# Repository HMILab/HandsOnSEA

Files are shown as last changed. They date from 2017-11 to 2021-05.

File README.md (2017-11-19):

# HandsOn-SEA

HandsOn-SEA is a single degree of freedom educational robot that features series elastic actuation and relies on closed loop force control to achieve the desired level of safety and transparency during physical interactions. HandsOn-SEA complements the existing impedance-type Haptic Paddle designs by demonstrating the challenges involved in the synergistic design and control of admittance-type devices. HandsOn-SEA can be used to allow students to experience the performance trade-offs inherent in force control systems, due to the non-collocation between the force sensor and the actuator.

For more information and videos please follow the [link](http://hmi.sabanciuniv.edu/?page_id=992).

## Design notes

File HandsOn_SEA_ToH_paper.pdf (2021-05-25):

IEEE TRANSACTIONS ON HAPTICS, VOL. X, NO. X, MAY 2021 | 1

# Physical Human-Robot Interaction Using HANDSON-SEA: An Educational Robotic Platform with Series Elastic Actuation

Ata Otaran | Ozan Tokatli | Volkan Patoglu

Abstract—For gaining proficiency in physical human-robot interactions, it is crucial for engineering students to be provided with the opportunity to gain hands-on experience with robotic devices that feature kinesthetic feedback. We propose HandsOn-SEA, a low-cost, single degree-of-freedom, force-controlled educational robot with series elastic actuation and introduce educational modules for the use of the device to allow students to experience the fundamental performance trade-offs inherent in robotic systems. The novelty of the proposed robot is due to the deliberate introduction of a compliant element between the actuator and the handle, whose deflections are measured to perform closed-loop force control. As an admittance-type robot, HandsOn-SEA relies on force feedback to achieve the desired level of safety and transparency and complements the existing impedance-type educational robots. We present the integration of HandsOn-SEA into the robotics curriculum, by providing guidelines for its use in a senior level robotics course, to help students experience the challenges involved in the synergistic design and control of robotic devices. We systematically evaluate the efficacy of the device in a robotics course delivered for five semesters and provide evidence that HandsOn-SEA is effective in instilling fundamental concepts and trade-offs in the design and control of robotic devices.

Index Terms—Physical Human-Robot Interaction (pHRI), Series Elastic Actuation (SEA), Educational Robotics, Interaction Control

I. INTRODUCTION
Establishing natural and safe physical human-robot interactions (pHRI) is an active research area. A thorough understanding of such interactions can be the basis of successful applications in many areas, including service robotics, surgical, assistive and rehabilitative robotics, haptics and teleoperation. Therefore, it is important for engineering students to have the opportunity to physically interact with robots to gain hands-on experience in their design and control. Hands-on experience is known to be crucial in strengthening the understanding of basic engineering concepts [1]. Haptic paddles [2]—single degree-of-freedom (DoF) devices with kinesthetic feedback—have been successfully utilized as effective teaching platforms for several system dynamics and controls classes in many universities around the world [3]. As educational tools, all haptic paddles share the common design features of simplicity, robustness and low cost. Design simplicity allows students to easily understand the working principles, while robustness and low cost enable their accessibility and availability for large groups of students.
In this paper, we introduce an educational force-feedback robot and provide guidelines for the educational use of the device to demonstrate the synergistic nature of mechanical design and control in robotic devices. We also present a set of laboratory assignments that allow students to experience the interdependency of design choices in the mechatronic design of robotic systems. These laboratory assignments require students to modify the mechanical system, in addition to its controller and characterize the effects of these design decisions on the closed-loop control performance of the educational device. We evaluate the efficacy of introducing HANDSON-SEA into robotics education by testing the device in a senior level robotics course delivered over five semesters and provide evidence that the
A. Otaran, O. Tokatli and V. Patoglu are with the Faculty of Engineering and Natural Sciences of Sabancı University, ˙Istanbul, Turkey.
E-mail: {ataotaran,otokatli,volkan.patoglu}@sabanciuniv.edu
Manuscript received May 30, 2020 and revised March 25, 2021.

device is effective in providing experience on fundamental concepts in robot control and instilling in a strong understanding of fundamental trade-offs in the design and control of force-feedback robotic devices. In comparison to its preliminary conference version [4], this paper details the mechatronics design, control, and performance of the device; significantly extends the guidelines for its educational use; evaluates the instructional design of the laboratory sessions through the achievement of course learning outcomes; and provides a systematic long-term evaluation of student performance and a comparison of this performance to a control group.

II. RELATED WORK

A. Design of Educational Devices with Haptic Feedback

Several open-hardware designs concerning force controlled robots exist in the literature. A pioneering educational force controlled robot designed for kinesthetic feedback is the haptic paddle [2]. The haptic paddle is a single DoF impedance-type device that features passive backdrivability and excellent transparency, thanks to its low apparent inertia and negligible power transmission losses. In the original design, a Hall effect sensor is used to sense rotations, while a custom built (analog) linear current amplifier is utilized to avoid torque ripple associated with PWM type motor drives. Other important design features of the haptic paddle are its robust design and low cost, thanks to utilization of common off-the shelf parts and simple rapid prototyping methods for its construction.
The success of this design has led to several different versions of the haptic paddle [5]–[10]. The original haptic paddle design relies on a capstan drive. However, the maintenance of the capstan transmission after cable stretch, fall-off or break is a tedious task, especially for an educational setup. To address these problems, the capstan transmission of the original design has been replaced by a custom built direct drive voice coil actuation in iTouch [5], [11], while a friction drive transmission has been adapted in [8].
In [6], improvements have been implemented to increase the design robustness and to decrease the manufacturing cost of haptic paddle. Further design iterations have been undertaken in [7], [9], [10], where especially the underlying electronics and control interface have been modified and updated. In particular, most of the earlier designs rely on PC based I/O cards and linear current amplifiers, while analog controller circuits are utilized in [5]. A PWM voltage amplifier and an Atmel processor (Arduino) based micro-controller are adapted in [8], trading-off the fast control rates of PC based controllers and torque control performance of linear current amplifiers with a more compact and low cost control/power electronics infrastructure. A recent iteration of these designs, the Hapkit [10], further customizes the control/power electronics infrastructure proposed in [8] and adds a force sensitive resistor to the device handle.
Haptic paddles aim at establishing safe and transparent pHRI. To achieve these goals, all of the designs reported in the literature rely on low inherent output impedance of the mechanical device. In particular, all of the existing haptic paddle designs are of impedance-type, possessing passive backdrivability thanks to their low friction power transmissions and low apparent inertia. Such impedance-type devices are commonly preferred for haptic interactions, since these devices can achieve high force control fidelity even with open-loop force control, that is, without the need for force feedback.
While HANDSON-SEA preserves the simplicity, robustness and low cost of other designs, as an admittance-type robotic device, it is fundamentally different from and complementary to all of the existing haptic paddles, as force feedback is an inherent design feature of HANDSON-SEA. Thanks to its integrated force estimation mechanism, HANDSON-SEA can utilize force feedback to modulate its output impedance for high fidelity haptic rendering. Due to its high transmission ratio, HANDSON-SEA is capable of rendering large forces at its handle, producing strong kinesthetic feedback that is easily differentiable by its users. As a result of its integrated force sensing element, HANDSON-SEA is inherently compliant, resulting in safe interactions even under impacts. The stiffness of the compliant element has a direct and observable effect on the performance of HANDSON-SEA and this compliance needs to be considered as part of its dynamic model and model based controllers.
B. Evaluation of Educational Devices with Haptic Feedback

Haptic paddles have been adopted to engineering curriculum by several universities [3]. The first investigation of a haptic paddle type device in a classroom/laboratory environment was conducted in [2]. In this work, haptic paddle has been proposed to support the learning process of students who have dominant haptic cognitive learning styles. The device was used for an undergraduate course on dynamic systems for a semester at Stanford University. The laboratory exercises included motor spin down test for observing the damping effect, bifilar pendulum test for understanding the components of the dynamic system, sensor calibration and motor constant determination, impedance control and virtual environment implementations. The laboratory modules of this work have formed a basis for other courses taught in different universities. The effectiveness of the haptic paddle was measured by a student survey and it has been observed that the device helped students to better grasp engineering concepts.
At the University of Michigan, force controlled devices iTouch and Box were used in engineering undergraduate courses [5]. In a mechanical engineering course, the device was used to support the learning of students about concepts such as frequency domain representations, dynamical system modeling and haptic interactions. In an electrical engineering course, students were introduced to integrating sensors and actuators to micro-controllers, learned about hybrid dynamical systems and improved their programming skills. Haptic paddle was also used in an undergraduate system dynamics course at Rice University [6], [12]. The use of the device aimed to improve the effectiveness of the laboratory sessions and to introduce students to haptic systems, where virtual environments can be used to assist the teaching of complex dynamics phenomena. In [6], student understanding of engineering concepts and fundamentals was quantified through a 16-item grading rubric during two semesters: a semester with traditional laboratory sessions disjointed from the course material and another semester during which haptic paddle was introduced to conduct a cohesive set of laboratory exercises. Results indicated important gains in student understanding with the integration of cohesive set of laboratory exercises with haptic paddles. In [12], a formal analysis was conducted over two semesters to investigate the effect of inclusion of reflective learning activities implemented through pre- and post-lab discussions. Performance was quantified through rubics, homework, laboratory, and final exam grades. Statistical analysis revealed that laboratory exercises with reflective learning activities resulted in statistically significant performance increase on the overall laboratory grades. While a significant effect was not shown for the final grades, reflective learning activities improved standard deviations and resulted in higher lowest grades. Another systematic evaluation of integrating haptic paddle in an undergraduate level pHRI course has been conducted in [7]. The pHRI course covered the effect of having a human in the loop, the design methodology for pHRI systems, system identification for the robotic devices, force controller design and assessment of the robot performance in terms of psychophysical metrics. Laboratory sessions included the implementation of open-loop and close-loop impedance controllers, gravity and friction compensation methods, and interaction controllers. Moreover, students were asked to complete course projects that combined the concepts they learned throughout the lectures. The effectiveness of the haptic paddle based instruction was measured by student evaluation surveys, oral exams and student presentations. It has been observed that hands-on learning was beneficial for pHRI and laboratory sessions can help students achieve higher degree of knowledge synthesis according to the Structure of Observed Learning Outcomes (SOLO) taxonomy. Furthermore, students’ evaluations of the device were positive, while the instructors observed an improved success rate in their exams.
Haptic paddle has also been used in an undergraduate system dynamics course at Vanderbilt University [8]. The laboratory sessions included analyzing first and second order system models, determining equivalent mass, damping and stiffness of these systems, exploring friction/damping and other external disturbances and observing their effects on the output of the system, experiencing the forced responses of vibratory systems, and implementing several closed-loop controllers. A formal assessment of student learning due to haptic paddle integration to the course was conducted over three semesters. To quantify student learning, assessments were administered before and after each semester. Furthermore, to determine the timing of learning, five multiple choice quizzes were administered in a randomized manner, before the lab, after the pre-lab, after the lab and after completing the lab report. Results showed a statistically significant difference with a large effect size between the cumulative scores at the beginning and at the end of the semester evaluations, indicating that students have gained a better understanding of and displayed better retention rates for the majority of the core concepts they learned throughout the course via all learning opportunities. The statistical analysis also revealed that supplementing the in-class lectures with laboratory sessions as a whole (including pre-lab, during lab, and lab report activities) enhanced student understanding of the material. The Stanford haptic paddle, called Hapkit, has been integrated as the main experimental setup in a massive open online course made accessible all around the world [10]. A newer version of Hapkit has also been used to teach physics in secondary education [13]. HANDSON-SEA complements all of these existing haptic paddles, not only in terms of its mechatronic design, but also as an educational tool, by enabling students to experience force-feedback control architectures for pHRI, and by demonstrating the synergistic design challenges involved in the mechatronic design of robotic devices. While HANDSON-SEA can be used to administer the laboratory exercises during a systems dynamics course as proposed in [2], [6], the unique design of HANDSON-SEA enables it to be used to demonstrate the interdependent nature of the plant and the controller dynamics on the system performance by allowing students to modify the plant in addition to its controller and characterize the effects of these design decisions on the closed-loop system performance. HANDSON-SEA is also effective tool to study the fundamental limitations of feedback control via demonstrations of strict stability limits under the non-collocation between the sensor and the actuator. HANDSON-SEA has been integrated into robotics education and has been under continual use in a classroom setting since 2016 [4].

III. DESIGN AND IMPLEMENTATION OF HANDSON-SEA

In this section, we detail the mechanical design, instrumentation and power electronics/control of HANDSON-SEA, a low-cost, single DoF educational robot with series elastic actuation (SEA). The design and controllers have been developed to promote a do-it-yourself philosophy [14]. All the design files and the software required to implement and operate HANDSON-SEA, as well as the assignments, laboratory manuals, and video demonstrations, are shared at https://github.com/HMILab/HandsOnSEA under MIT General Public License. Files are regularly being updated for wider availability, lower manufacturing cost, and better robustness. Furthermore, open-source hardware allows end users to share, customize, and improve designs.

A. Mechanical Design and Power Transmission

The main actuation mechanism and dimensions of HANDSON-SEA, as presented in Figure 1, have been designed to be compatible with existing haptic paddle designs, such that existing devices can be equipped with SEA with minimal modifications. To enable builtin force sensing, the sector pulley, which is common to almost all haptic paddle designs, has been modified to feature a compliant joint element and a position sensor to measure deflections of this compliant element.
In particular, the monolithic rigid sector pulley-handle structure has been manufactured in two parts: the handle with a Hall effect sensor and the sector pulley with two neodymium block magnets. The handle is attached to the device frame through a ball-bearing, and the sector pulley is attached to the handle through a cross-flexure pivot. A cross-flexure pivot, formed by crossing two symmetrical leaf springs, is a robust and simple compliant revolute joint with a large range of deflection [15], [16]. A cross-flexure pivot is preferred as the compliant element of the SEA since this leaf-spring type compliant pivot distributes stress over its entire length and provides robustness by avoiding stress concentrations that are inherent in notch-type compliant elements. The center of rotation of the cross-flexure pivot is aligned with the rotation axis of the handle, while the Hall effect sensor is constrained to move between the neodymium block magnets embedded in the sector pulley.
As in haptic paddle designs, the sector pulley of the device can be actuated by a capstan drive or a friction drive transmission. In our current prototype, we prefer to use a friction drive power transmission, since it is more robust and easier to maintain. Furthermore, even though it has been shown that friction and slip due to friction drive transmission can significantly decrease the rendering performance of haptic paddle devices operating under open-loop impedance

T
L

2α
W

(b)

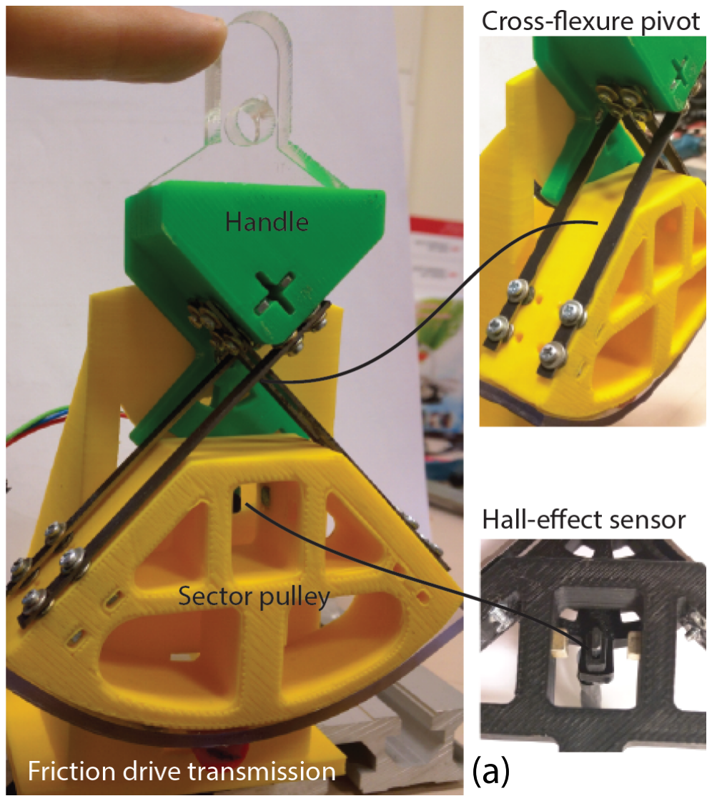
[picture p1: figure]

(a) (b)
Fig. 1: a) HANDSON-SEA – A single DoF series elastic educational robot b) An exaggerated finite element model of the proposed compliant element and its schematic representation with parameters control [9], these parasitic effects caused by the low quality power transmission element can be more effectively compensated by the robust cascaded control architecture of SEA [17].
Our current design employs a surplus geared coreless DC motor (Maxon RE 13 with 84:1 gearbox) equipped with an encoder together with a friction drive to impose desired motions to the sector pulley. In order to keep the manufacturing simple and low cost, all the mechanical components of the educational robot, except for the sheet metal parts and the bearing, are designed to be suitable for construction using additive manufacturing techniques. The design consists of simple planar parts that can be fabricated using low cost methods, such as laser cutting. A capstan drive version of HANDSON-SEA with an alternative low-cost DC motor, as well as multi-DoF versions inspired by [11], are presented in [14].
B. Sensors and Power Electronics
HANDSON-SEA necessitates two position sensors: one for measuring the motor rotations and another for measuring the deflections imposed on the elastic element. Since the surplus DC motor used readily includes a magnetic encoder, this sensor is used for measuring motor rotations and estimating motor velocities. The deflections of the cross-flexure pivot are measured using a Hall-effect sensor (Allegro MicroSystems UNG3503). A simple and low cost Hall-effect sensor is appropriate for measuring these deflections, since the required range for measurements is small, resulting in robust performance. Furthermore, from a pedagogical point of view, this choice enables students to gain experience in integrating both analog (Hall effect) and digital (magnetic digital encoder) sensors into the control system. A low cost PWM voltage amplifier (TI DRV8801 H-bridge motor driver with carrier) is utilized to drive the DC motor. Unlike the impedance type haptic paddle designs, this selection is not a compromise solution for our design that trades-off performance for cost effectiveness. On the contrary, a PWM voltage amplifier is a natural choice for the cascaded loop control architecture of SEA, since the velocity (not the torque) of the motor is controlled by the inner motion control loop and any high frequency vibrations (possibly induced by PWM) are mechanically low-pass filtered by the compliant element before reaching to the user.
C. Micro-Controller
We have implemented controllers for the series elastic robot using a low-cost micro-controller, TI C2000 (LaunchpadXL-F28069M). We have interfaced HANDSON-SEA with and implemented its cascaded loop controller using TI Launchpad, since this cost effective industrial grade controller can decode quadrature encoders and can be used to effectively estimate velocities from encoder measurements. Furthermore, this micro-controller can be programmed through the Matlab/Simulink graphical interface, and allows for easy prototyping of (multi-rate) control architectures with hard real-time performance.

IV. MODELING AND CONTROL OF HANDSON-SEA

A. Stiffness of the Cross-Flexure Pivot
Figure 1(b) presents a schematic model of the cross-flexure pivot. Five parameters govern the deflection and stiffness properties of a cross-flexure pivot: The length L, the thickness T and the width W of the leaf springs, the angle 2α at the intersection point of the leaf springs and the dimensionless geometric parameter λ ∈ [0, 1] that defines the distance of the intersection point of leaf springs from the free end. Given these parameters, the torsional stiffness Kτ of the cross-flexure pivot can be estimated as follows [16], [18], where E is the modulus of elasticity and I is the second moment of area.

Kτ = 8(3λ

2 − 3λ + 1)EI
L

(1)

TABLE I: Parameters Used for Dynamic Modeling

Ja – inertia of the motor | 1.3 | gr-cm²
Jg – inertia of the gearhead | 0.05 | gr-cm²
Jh – inertia of the handle about the bearing | 1.93 | gr-cm²
Jp – inertia of the sector pulley about the bearing | 14.7 | gr-cm²
rg – gearhead reduction ratio | 84:1
rc – capstan reduction ratio | 73:9
kf – stiffness of the cross flexure pivot | 4000 | N-mm/rad
R – motor resistance | 10.7 | Ohm
bm – cumulative damping of the motor | 0.025 | N-mm/s
Km – motor torque constant | 16.2 | mN-m/A
Kb – motor back-emf constant | 61.7 | rad/sec/V
τm – mechanical time constant | 5.31 | ms
B. Dynamic Model
The series elastic robot can be modeled as a single link manipulator actuated by a DC motor. Table I defines and lists the parameters that are relevant for dynamical modeling of HANDSON-SEA.
The motion of the DC motor is controlled by regulating its voltage. Since the electrical time constant (0.042 ms) of the DC motor is two orders of magnitude lower than its mechanical time constant (5.31 ms), the transfer function from motor voltage V (s) to motor velocity sθm(s) can be derived as

sθm(s)
V (s)

=

Km/R
Js + b

(2)

where J = Jm + Jg + Jp/(rgrc)

2
and b = bm + KmKb/R. Note
that we have neglected the inertial contribution of the handle, since its inertia Jh is also orders of magnitude smaller than the reflected inertia of the motor side of the cross-flexure pivot. Neglecting the inertial contributions of Jh, the torque τh measured by the flexure acts on the system according to

sθm(s)
τh(s)

=

−1/(rgrc)
Js + b

(3)

where the rotation of the pulley is related to the motor rotation by θp(s) = θm(s)/(rgrc). Unmodeled dynamics of the system are considered as disturbances that act on the system. Robust motion control of the DC motor is used to compensate for these disturbances.

C. Cascaded Loop Controller
The SEA controller is based on cascaded control loops, which has first been proposed in [19] and later rediscovered in [20], [21]. In this approach, also called velocity-sourced impedance control (VSIC), the inner loop of the control structure employs a robust motion controller to compensate for the imperfections of the power transmission system, such as friction, stiction and slip, rendering the motion controlled system into an ideal velocity source within its control bandwidth. The intermediate control loop incorporates force feedback into the control architecture and ensures good force tracking performance under an adequately designed inner loop. Finally, the outer loop determines the effective output impedance of the system. For the cascaded control architecture, the controller parameters are selected according to [17], [22], [23]. These control parameters satisfy the necessary and sufficient conditions for frequency domain passivity of the system during null space and stiffness rendering and ensure coupled stability of interactions with SEA.
Table II summarizes the experimentally characterized technical specifications of HANDSON-SEA. The velocity, small force and large force bandwidths of HANDSON-SEA are verified to be 14 Hz, 12 Hz, and 7 Hz, respectively. Characterizations with a commercial force sensor (ATI Nano 17) verify these results and indicate that steady state error for HANDSON-SEA is less than 5% for set-point force control, while the force tracking RMS error of HANDSON-SEA is characterized as 7.6% for a chirp signal up to 3 Hz.

TABLE II: Technical Specifications of HANDSON-SEA

Continuous Force Output at the Handle | 15 | N
Deflection Sensing Resolution (Hall) | 0.2 | mm
Force Sensing Resolution | 0.05 | N
Workspace | ±40 | ◦
Nominal Speed at Gear Output | 145 | rpm
Velocity Control Bandwidth | 14 | Hz
Small Force Bandwidth | 12 | Hz
Large Force Bandwidth | 7 | Hz
V. LABORATORY ASSIGNMENTS WITH HANDSON-SEA

HANDSON-SEA has been designed to enable students to experience the synergistic coupling between the plant and the controller dynamics on the overall performance of mechatronic systems. Series elastic actuators are inherently multi-domain systems whose performance depends on the design of both the plant and the controller [24]. Hence, these devices are well suited for demonstrating the challenges involved in the design of robotic systems and instilling in the importance of concurrent design thinking to achieve the best performance from mechatronic devices.
The senior level Introduction to Robotics course at Sabanci University is designed to equip students with the fundamental theories and the computational methodologies that are used in design and analysis of robotic systems. Students learn how to analytically formulate kinematic and dynamic equations for robot manipulators, how to model actuator and drive train dynamics, synthesize trajectory tracking and interaction controllers, as well as how to utilize numerical algorithms to simulate and real-time hardware-in-the-loop controllers to implement such closed-loop control systems. The emphasis in the course is an integrated understanding of the kinematic/dynamic modeling and control concepts for robotics.
In the control part of the robotics course that utilizes HANDSON-SEA, students are first introduced to fundamental limitations imposed due to the non-collocation of sensors and actuators. It is noted that while non-collocation arises in motion control systems with drive train dynamics, this limitation is inherent to all causal systems with force feedback [25]–[27]. After the introduction of the fundamental limitations, the concept of series elastic actuation is explained as a trade-off between the sensor stiffness and controller gains, emphasizing the interdependence of the mechanical and controller design. It is noted that SEA trades-off large force-control bandwidth for force/impedance rendering fidelity, by using compliant force sensing elements in the force control framework [19], [28]. By decreasing the force sensor stiffness and utilizing a model of the compliant element, higher force-feedback controller gains can be utilized to achieve responsive and robust force-controllers within the control bandwidth of the system. It is explained that SEA possesses favorable output impedance characteristics, allowing it to be safe for human interaction over the entire frequency spectrum. In particular, within the force control bandwidth of the device, SEA can ensure backdrivability through active force control, that is, by modulating its output impedance to the desired level. For the frequencies over the control bandwidth, the apparent impedance of the system is limited by the inherent compliance of the force sensing element, which acts as a physical filter against impacts, impulsive and high frequency disturbances (such as torque ripples). The main disadvantage of SEA is emphasized as its relatively low large-force bandwidth, caused by actuator saturation due to significant sensor compliance.
A set of laboratory assignments have been developed as six main modules to complement the theoretical concepts covered in the Introduction to Robotics course. The laboratory sessions were held under the supervision of two graduate students who helped to solve any technical problems, spark pre- and post-lab discussions, and encourage equal participation by group members. After the basic concepts have been covered during lectures, students were given pre-laboratory assignments to complete as a warm-up to key concepts before they attended the laboratory sessions.
The course learning outcomes (CLO) for these laboratory sessions are defined as: “By the end of the laboratory sessions, students will be able to model actuator and drive train dynamics, synthesize trajectory tracking and interaction controllers (CLO-1), and utilize numerical algorithms to simulate, and real-time hardware-in-the-loop controllers to implement closed-loop control systems (CLO-2).”
The laboratory modules can be summarized as follows:
Module 1: This module is designed to study the modeling, control, and experimental characterization of a single DoF dynamic rigid body system under motion control. In the pre-laboratory assignments to be completed before this module, students reviewed the concepts of transfer functions, root-locus and Bode plots.
During this module, firstly, the students derived the second order rigid body model of the plant with the DC motor and investigated the theoretical stability limits of the motion controlled system through a root-locus analysis. They concluded that instability is not expected even for high controller gains, since the root-locus plot of the position controlled rigid-body model has two asymptotes. They determined the theoretical controller gains to achieve a pre-determined bandwidth with no overshoot.
Secondly, students implemented a PI velocity controller for the motor of HANDSON-SEA and tried the controller gains they had calculated analytically. They empirically tuned their controllers to achieve the fastest stable non-overshooting step response. They were asked to discuss possible reasons of instability they experienced for large gains during the physical implementation of the controller. Actuator bandwidth limitation, unmodeled dynamics of the device, sampling-hold effects and sensor noise were explained as some of the potential factors behind the practical gain limits. The effect of bandwidth limitation due to the saturation of the actuator was demonstrated using a first order low-pass filter at the actuator input in simulation and with a root-locus analysis.
In the final step, students collected data with the empirically tuned gains and drawed a Bode plot of the system to determine the closed-loop velocity control bandwidth of the device. It was discussed that, up to this frequency, the robot can be regarded as a perfect velocity source, as necessitated by the force and impedance control loops. Module 2: This module is designed to demonstrate the fundamental stability limits of closed-loop control systems that possess sensor actuator non-collocation. In the pre-laboratory assignments, students studied non-collocated motion control of systems with drive train dynamics and were exposed to explicit force control.
During this module, the students implemented an explicit force controller by utilizing the force feedback obtained by measuring the deflections of the series elastic element. While testing this controller, students experienced that the control gains need to be kept low, not to induce instability and chatter during contacts. This phenomenon was attributed to the non-collocation between the force sensor and the motor, and students were asked to model this non-collocation by a linear model that captures the first vibration mode of the system. Root-locus analyses enabled students to observe that non-collocation introduces two poles and one zero to the system, thus an additional asymptote, which causes the close loop poles to become unstable for high loop gains. Students also analysed two alternative linear models that result from introducing compliance to the robot base or the environment. In these analyses, they observed that the same number of poles and zeros are introduced to the system. Upon finishing this module, students were expected to convince themselves that the instability was caused by the compliance specifically located between the actuator and the sensor.

Module 3: This module is designed to provide students with an understanding of the interdependent nature of plant and controller dynamics in the design of robotic systems. Along these lines, the fundamental trade-off between the physical sensor stiffness and the maximum stable force controller gain is studied.
In the pre-laboratory assignments, students were introduced to the analytical stiffness model of the cross flexure joint and reviewed root-locus based stability analysis of force controlled systems with non-collocation.
During this module, firstly, students calculated the stiffness of the two different flexure joints. One of the cross flexure joints featured two leaf springs with λ = 0.5 and possessed a low stiffness. The other cross flexure joint featured four leaf springs with λ = 87.3%, had low center shift, better lateral stability, and significantly higher stiffness. In general, capstans with different stiffness levels can be implemented by simply changing the thicknesses and/or the number of the leaf springs used to form the compliant joint.
Secondly, students utilized the cross flexure joint with higher stiffness in an explicit force controller to empirically determine the maximum controller gain that can be used without inducing instability or chatter during contacts. The same procedure was repeated for the cross flexure joint with lower stiffness. The loop gains were computed for both cases, such that students could experimentally verify that decreasing the force sensor stiffness enabled them to increase the force controller gains. Finally, the advantages and disadvantages of using a more compliant force sensor were discussed, from the perspectives of the coupled stability and force control performance. Module 4: This module is designed to study the SEA concept and trade-offs involved in their design. Furthermore, this module provides hands-on experience with SEA to demonstrate the output impedance characteristics and the bandwidth of these systems.
In the pre-laboratory assignments, the underlying idea of SEA was explained as the reallocation of limited loop gain of the non-collocated force control system, implemented by decreasing the physical force sensor stiffness by a few orders of magnitude, such that the force controller gain can be increased by a similar amount. It was noted that higher feedback controller gains are preferred to achieve fast response times and good robustness properties to compensate for hard to model parasitic effects, such as friction and backlash. The trade-off involved in this decision was also emphasized by a discussion of the actuator saturation and bandwidth limitation arising due to the use of a more compliant force measurement unit. The output impedance transfer function of the system was derived and its Bode plot was studied to characterize the system behaviour at low and high frequencies.
During this module, students implemented an actively backdrivable system by setting the desired force in the explicit force controller to zero. Next, they pushed the handle of the device with low, intermediate and high frequency (impulsive) inputs. The same procedure was repeated when the controller was turned off. The students were asked to comment on the changes they experience in the output impedance with the gradual increase in frequency for both cases.
Next, students applied high frequency torque ripples through the motor while holding the handle to experience the low pass filtering behaviour of SEA. They also plotted the data collected by the force sensing element during this input and compared it with the torque ripple input, to better visualize the filtering effects. Finally, students implemented and characterized set point controllers to determine the force control performance of SEA.
Module 5: This module is designed to introduce the cascaded controller architecture for SEA and to evaluate the rendering and force tracking the performance of the device under VSIC.

In the pre-laboratory assignments, the rationale behind the cascaded controller was explained. The necessary and sufficient conditions for the controller gains to ensure coupled stability of the system are also briefly discussed as in [17], [22], [23].
During this module, students implemented impedance controllers with the cascaded control architecture, to render free space, virtual walls and a mass-spring-damper system, respectively. In particular, in the cascaded controller, the desired impedance was set to zero for free space rendering, such that the system tried to achieve ideal active backdrivability. The desired impedance was set to that of relatively stiff unidirectional springs to render virtual walls. During stiffness rendering, through attachment of a sufficiently large mass to the handle, it was demonstrated that the stiffness of the virtual wall cannot be set higher than the stiffness of the cross flexure joint, to ensure coupled stability of interaction. The desired impedance was set to a second order system dynamics to render a mass-spring-damper system. Students were asked to compute the natural frequency of the virtual mass-spring-damper system and verify through physical interaction that the virtual system had a resonance at this frequency. To complement haptic rendering exercises, animations were provided to students to help them visualize the dynamical system that governed the haptic feedback. Finally, students were asked to characterize the force tracking the performance of SEA for chirp reference signals. Module 6: This module aims to demonstrate the performance trade-offs of SEA by letting students characterize the closed-loop force control bandwidth of the device under various loads.
In the pre-laboratory assignments, students reviewed the experimental determination of Bode plots. The concept of small and large force bandwidths were introduced, and the trade-offs involved in the determination of the stiffness of the SEA were discussed.
During this module, students experimentally characterized the small and large force bandwidths of the device by providing sinusoidal references to the system and recording its response, for force references of various magnitudes. Students were expected to experience a decline in the system bandwidth as the magnitude of the desired force increases. The effect of actuator speed saturation was emphasized as the underlying reason. Increasing the sensor stiffness, decreasing the damping in the system, and increasing the velocity bandwidth of the actuator were discussed as possible remedies.

VI. EVALUATION OF EDUCATIONAL EFFICACY

The educational effectiveness of the laboratory assignments has been evaluated through student surveys, course learning outcomes and student performance measured at the final exam.

A. Student Evaluations of HANDSON-SEA
We have used HANDSON-SEA while teaching the Introduction to Robotics course at Sabanci University during Spring 2016, Fall 2016, Fall 2017 and Fall 2018 semesters. These 4 semesters included 81 students with mechatronics background, while 46 students who took the course during Spring 2015 semester served as the control group. The course has been taught in all of these five semesters by the same instructor, while the laboratory assignments with HANDSON-SEA as detailed in Section V have been integrated into the curriculum from Spring 2016 onwards. As a pre-requisite of the course, all of the students had completed at least one course on system dynamics and one course on feedback controls; but none of them had any background on force control or SEA.
During the laboratory sessions of the course, Modules 1–6 were implemented utilizing HANDSON-SEA. The course also included lectures that cover relevant technical concepts in these modules, weekly recitation hours, and pre-laboratory assignments. After the

TABLE III: Survey Questions and Summary Statistics

Q1: What kind of knowledge and skills did you require to use HANDSON-SEA? Frequency
Knowledge of modeling dynamical systems | | 66.8%
Knowledge on controls theory | | 73.5%
Familiarity with hardware-in-the-loop | | 68.9%
Experience with real-time controllers | | 64.3%
Experience with motor drivers | | 56.1%
Experience with integrating sensors | | 55.5%
Experience in programming | | 54.6%

Q2: Which one of the following aspects of HANDSON-SEA do you find important?
| | Frequency
Easy to use | | 77.8%
Simple working principle | | 76.0%
Robust | | 68.3%
Low cost | | 82.4%
User friendly | | 70.9%
Easy to build and maintain | | 78.1%

Q3: How would you rate the usefulness of HANDSON-SEA for the following groups?
Mean = 3.94 | σ
| | 2 = 1.02
Mechatronics juniors and seniors | 4.40 | 0.92
Mechatronics graduates | 4.31 | 0.88
High school students | 2.10 | 1.21
Robotics researchers | 4.10 | 1.02

Q4: How useful were HANDSON-SEA in helping with the following concepts and trade-offs?
Mean = 4.12 | σ
| | 2 = 0.91
Compliant mechanisms | 4.15 | 0.93
Sensor actuator non-collocation | 4.18 | 0.88
Fundamental limitations of force control—compliance-gain trade-off | 4.30 | 0.83
Admittance control | 4.23 | 0.89
Series elastic actuation | 4.17 | 0.99
Backdrivability and output impedance | 4.16 | 0.92
Cascaded loop control and role of inner loop on robustness | 3.66 | 1.06
Trade-off between control bandwidth and force sensing resolution | 4.13 | 0.86
Small and large force bandwidth | 4.11 | 0.86

Q5: Please rate the usefulness of the following aspects of HANDSON-SEA.
Mean = 3.91 | σ
| | 2 = 0.96
Integrated force sensor | 3.94 | 0.93
No required experience with real-time programming | 3.54 | 1.04
Ability to change controller gains and sensor stiffness | 4.12 | 0.89
Velocity estimation in hardware | 3.74 | 1.03
Integration with Matlab/Simulink | 4.21 | 0.93
Implemented cascaded controller | 3.89 | 0.96

course, all students filled in an anonymized questionnaire. The questionnaire includes 5 questions: Q1 is aimed at evaluating the background required by the students, Q2 is for assessing the useability of the device, Q3 is for determination of target population for its educational use, and Q4–Q5 are for assessing the useful aspects of HANDSON-SEA. For Q1 and Q2, the participants were allowed to choose all responses that apply, while for Q3–Q5, five-point Likert scale, ranging from “1” strong disagree to “5” strong agree, has been used to measure the agreement level of the participants.
Questions together with their summary statistics are presented in Table III. The Cronbach’s α values have been calculated for the each part of the survey; all α values, except for Q3, are evaluated to be greater than 0.7, indicating a high reliability of the survey. It is observed that, due to the increase in the sample size, the reliability of the survey has improved compared to the preliminary results in [4]. A high Cronbach’s α is not expected for Q3 as the participants tend to rank their preferences for this question, rather than separately rating each choice. Ranking the choices naturally results in a low Cronbach’s α, since a high Cronbach’s α is attained when the variance of answers to the same question is low and the variance between the total points is high.
The main results of the survey can be summarized as follows:
- Responses to Q1 indicate that knowledge of dynamic systems and controls theory is essential, while some hands-on experience with programming and hardware is useful.
- In Q2, students indicated that they find simple working principle, robustness, and user-friendliness as important aspects.
- Responses to Q3 indicate that students evaluated the modules to be useful for mechatronics students and robotics researchers.
- Answers to Q4 provide evidence that students evaluate the modules effective in helping them learn fundamental concepts and trade-offs in robotics. In particular, the mean scores averaged over all concepts indicate that students agreed that HANDSON-

SEA helped them understand concepts in general, while the mean scores for individual concepts show that proposed modules were perceived as effective for teaching each of these concepts.
- For Q5, the mean scores of individual features indicate that students appreciated the fact that HANDSON-SEA provides them with integrated force and velocity sensing, a simple programming interface, and easy-to-use controllers.
B. Effect of HANDSON-SEA on Student Performance
In addition to the survey results that capture students’ perceptions and evaluations, we have also studied the course learning outcomes and the effect of HANDSON-SEA on student performance by comparing student final exam grades when the course has been taught with and without utilizing HANDSON-SEA.
Following questions that require a high degree of knowledge synthesis according to SOLO taxonomy were asked in the final exams: “Explain sensor actuator non-collocation and why it detrimentally impacts the controller performance. Discuss why explicit force control systems inherently possess sensor actuator non-collocation.”
The student performances on this final exam question for the five semesters were compared. Figure 2 presents the distribution of grades per semester, verifying the consistency and close to normal distribution of grades for different semesters. A one-way ANOVA was conducted to determine the significance of HANDSON-SEA on the quantitative final exam question grades over different semesters. ANOVA results indicate that the effect of the semester is significant with F(4, 124) = 5.48, p < 0.0004. Tukey’s honestly significant difference procedure was employed for multi-comparisons, as it is known to be a conservative method for one-way ANOVA with different sample sizes. Multi-comparisons results indicate that student performance in Spring 2015 when HANDSON-SEA was not used is significantly worse than all other terms when HANDSON-SEA was used. In particular, in Spring 2015, students scores have a mean of 29.3% with a 6.21% standard deviation, while the mean has significantly increased to 66.1% with an 11.3% standard deviation in Spring 2016, to 64.5% with a 7.67% standard deviation in Fall 2016, to 70.6% with a 10.2% standard deviation in Fall 2017, and 61.8% with a 9.67% standard deviation in Fall 2018, respectively. The effect size is significant as the scores have more than doubled with the introduction of HANDSON-SEA to the laboratory curriculum. The achievement of course learning outcomes for the laboratory sessions (introduced to the course evaluations with the Spring 2016 updates) is reported in Table IV as a second metric. On average more than 70% of students displayed satisfactory or better competence on CLO-1 and CLO-2, indicating high success of the instructional design of the laboratory sessions with HANDSON-SEA.

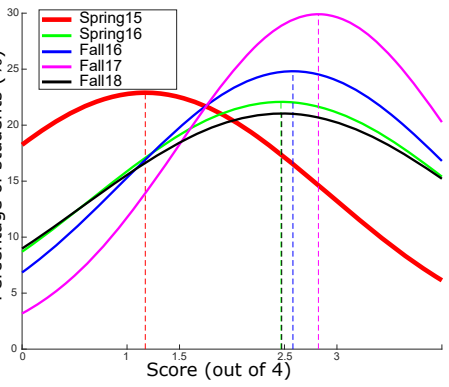
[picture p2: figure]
Spring15; Spring16 Fall16 Fall17 Fall18; Score (out of 4)

Percentage of students (%) Fig. 2: Distribution of exam grades per semester

TABLE IV: Achievement of Laboratory Session Learning Outcomes

Term | Total # | # successful | % successful | # successful | % successful
| of students | at CLO-1 | at CLO-1 | at CLO-2 | at CLO-2
Spring 2016 | 15 | 11 | 73% | 11 | 73%
Fall 2016 | 31 | 22 | 71% | 23 | 74%
Fall 2017 | 17 | 13 | 76% | 12 | 71%
Fall 2018 | 28 | 20 | 71% | 21 | 75%

To rule out the effects of external variables as much as possible, we note that students are admitted to Sabanci University based on academic merit, through a nationwide centralized exam and the performance of the student population does not vary significantly among the classes of 2015, 2016, 2017 and 2018, as evidenced by overall student performance metrics carefully monitored by the university. The Introduction to Robotics has been delivered by the same instructor since 2012, course materials have already been fully developed by Spring 2015, and no fundamental changes (other than the introduction of laboratory sessions with HANDSON-SEA in Spring 2016) has been introduced since then. The teaching performance monitored though standard teaching evaluations administered by Sabanci University rectorate remained consistent throughout Spring 2015–Fall 2018. Furthermore, students taking the course were assigned a sample exam that provided comprehensive a list of the fundamental concepts that are essential in the study of robotic systems.
While the ordering effect cannot be completely eliminated, as it would not be fair to students who are not provided with the opportunity of experiencing the laboratory assignments, a closer analysis of last four semesters with HANDSON-SEA shows that student performance did not change significantly during this period, indicating the change in performance can be most likely be attributed to the laboratory assignments with HANDSON-SEA.

VII. DISCUSSION AND CONCLUSION
HANDSON-SEA has been systematically evaluated in a senior level robotics course and shown to be effective in teaching some of the fundamental concepts in robotics. High success rate of CLOs indicate that instructional design of the laboratory sessions are effective. Furthermore, the statistically significant increase in student final exam scores with a meaningful effect size indicate that laboratory modules with HANDSON-SEA are beneficial and can help students learn and retain theoretical core concepts more effectively.
In [2], [7] anecdotal case studies, qualitative surveys, and instructor experiences have been provided to show perceived value of haptic paddle devices. It has been argued that haptic paddles improve student enthusiasm, enable hands-on experience, and help materialize abstract concepts. Our results are in good agreement with these experiences. In [6], the effect of a cohesive set of laboratory exercises with haptic paddles on student understanding of engineering concepts with respect to traditional disjoint labs was studied over two semesters. While a formal analysis is lacking, trends based on grading rubics indicated that important gains in student understanding can be achieved with a cohesive set of laboratory exercises. In [12], a formal analysis was conducted over two semesters to investigate the effect of inclusion of reflective learning activities to laboratory sessions, and a statistically significant performance increase on the overall laboratory grades has been demonstrated. Similar to [6], we compared student performance with and without HANDSON-SEA integration over multiple semesters. Our results support the findings in [6] and extends them by providing a statistically significant improvement on the final exam scores, indicating students learned and retained theoretical core concepts more effectively when haptic educational devices were used as a part of cohesive set of laboratory exercises. Similar to [12], our laboratory sessions included pre- and post-lab assignments with discussions and high success rate of CLOs indicate that instructional design of the laboratory sessions were effective. While the introduction of haptic paddles to the laboratory sessions in [12] did not result in statistically significant changes in knowledge transfer measured through exam performance, our study provides such significant results, as exam questions has been included in the design of the study, student performance was compared for with and without HANDSON-SEA integration, resulting in a fundamental change in the laboratory sessions, and the study has been conducted over five semesters to reach to a sufficiently large sample size. Similar to [8], our study includes a formal assessment of student learning due to haptic paddle integration conducted over multiple semesters and provide statistically significant difference with a large effect size between student scores. Unlike [8], our study did not aim to determine the timing of learning, but it included a control group to which the course has been delivered without the integration of the haptic paddle. Our results are also in good agreement with [8], as the laboratory sessions significantly improved student performance. Overall, this study complements other studies in that, formal evaluations over multiple semesters have been conducted to compare student performance with a control group to which the course has been delivered without the integration of HANDSON-SEA and statistically significant effects on student performance has been provided as an evidence of student learning, under the fundamental assumption that performance is a good proxy of learning.
The instructor experiences of teaching the course with and without laboratory assignments utilizing HANDSON-SEA also strongly indicate that, instilling in physical intuition, HANDSON-SEA is helpful to support higher-order learning of students. In particular, before the laboratory assignments with HANDSON-SEA, it has been challenging to achieve a solid understanding by students about the synergistic nature of the plant and the controller dynamics on the robotic system performance, and the fundamental limitations introduced by feedback control. After the lectures have been supported by laboratory exercises utilizing HANDSON-SEA, the interdependent nature of the plant and the controller dynamics can easily be demonstrated by changing the physical stiffness of the device, while a fundamental limitation of feedback control can be discussed through the stability bounds under non-collocation.
During the pandemic, low cost design of HANDSON-SEA has been useful to enable online laboratory sessions by sending a device to each registered student. HANDSON-SEA has also been utilized in the graduate level Force Control and Bilateral Teloperation course at Sabanci University for multiple semesters. Furthermore, HANDSON-SEA has been instrumental in promoting students to work on force controlled robotic applications for their graduation projects, by removing the high cost hardware barrier for developing devices with high force output capabilities and speeding up the project development process. HANDSON-SEA provides a rich platform for design courses, as it possesses many modifiable features along with a simple and robust design that allow students to experience all the design stages, namely determination of design criteria, mathematical modeling, mechatronics design, instrumentation and implementation. To date, over 24 students have completed their graduation projects using HANDSON-SEA and implemented various force-feedback devices with significant impact on technology development, including a haptic pedal feel platform for driving under regenerative braking [29]. Overall, HANDSON-SEA is an open-source force-feedback educational robot that has the potential to be beneficial for the education of a diverse set of concepts in haptics and robotics communities.

REFERENCES

[1] Z. Dogmus, E. Erdem, and V. Patoglu, “ReAct!: An interactive educational tool for AI planning for robotics,” IEEE Transactions on

Education, vol. 58, no. 1, pp. 15–24, 2014.
[2] A. M. Okamura, C. Richard, and M. R. Cutkosky, “Feeling is believing: Using a force-feedback joystick to teach dynamic systems,” Journal of Engineering Education, vol. 91, no. 3, pp. 345–349, 2002.
[3] W. Provancher, “Eduhaptics.org,” Online, 2012, http://eduhaptics.org.
[4] A. Otaran, O. Tokatli, and V. Patoglu, “Hands-on learning with a series elastic educational robot,” in Eurohaptics, July 2016.
[5] R. Gillespie, M. Hoffman, and J. Freudenberg, “Haptic interface for hands-on instruction in system dynamics and embedded control,” in IEEE Haptics Symposium, 2003, pp. 410–415.
[6] K. Bowen and M. K. O’Malley, “Haptic interfaces for a Labview-based system dynamics course,” in ASEE Conference and Exposition, 2006.
[7] R. Gassert, J. Metzger, K. Leuenberger, W. Popp, M. Tucker, B. Vigaru,
R. Zimmermann, and O. Lambercy, “Physical student-robot interaction with the ETHZ Haptic Paddle,” IEEE Transactions on Education, vol. 56, no. 1, pp. 9–17, 2013.
[8] J. L. Gorlewicz, L. B. Kratchman, and R. J. Webster III, “Haptic paddle enhancements and a formal assessment of student learning in system dynamics,” Advances in Eng. Education, vol. 4, pp. 186–217, 2014.
[9] C. Rose, J. French, and M. O’Malley, “Design and characterization of a haptic paddle for dynamics education,” in IEEE Haptics Symposium, 2014, pp. 265–270.
[10] T. Morimoto, P. Blikstein, and A. Okamura, “Hapkit: An open-hardware haptic device for online education,” in IEEE Haptics Symposium, 2014.
[11] R. B. Gillespie, T. Shin, F. Huang, and B. Trease, “Automated Characterization and Compensation for a Compliant Mechanism Haptic Device,” IEEE Transactions on Mechatronics, vol. 13, no. 1, pp. 15–24, 2008.
[12] C. G. Rose, C. G. Mcdonald, J. P. Clark, and M. K. O’Malley, “Reflection on system dynamics principles improves student performance in haptic paddle labs,” IEEE Transaction on Education, vol. 61, no. 3, pp. 245–252, 2018.
[13] M. O. Martinez, T. K. Morimoto, A. T. Taylor, A. C. Barron, J. D. A. Pultorak, J. Wang, A. Calasanz-Kaiser, R. L. Davis, P. Blikstein, and
A. M. Okamura, “3D printed haptic devices for educational applications,” in IEEE Haptics Symposium, 2016, pp. 126–133.
[14] A. Otaran, “Design, control and evaluation of educational devices with series elastic actuation,” MSc. Thesis, Sabanci University, 2017.
[15] W. H. Wittrick, “The properties of crossed flexural pivots and the influence of the point at which the strip cross,” The Aeronautical Quarterly II, pp. 272–292, 1951.
[16] O. C. Kara and V. Patoglu, “VnStylus: A haptic stylus with variable tip compliance,” IEEE Transactions on Haptics, 2020.
[17] F. E. Tosun and V. Patoglu, “Necessary and sufficient conditions for the passivity of impedance rendering with velocity-sourced series elastic actuation,” IEEE Transactions on Robotics, vol. 36, pp. 757–772, 2020.
[18] Z. Hongzhe and B. Shusheng, “Accuracy characteristics of the generalized cross-spring pivot,” Mechanisms and Machine Theory, vol. 45, pp. 1434–1448, 2010.
[19] R. D. Howard, “Joint and actuator design for enhanced stability in robotic force control,” Ph.D. dissertation, MIT, 1990.
[20] G. Pratt, P. Willisson, C. Bolton, and A. Hofman, “Late motor processing in low-impedance robots: impedance control of series-elastic actuators,” American Control Conference, pp. 3245–3251, 2004.
[21] G. Wyeth, “Demonstrating the safety and performance of a velocity sourced series elastic actuator,” in IEEE ICRA, 2008, pp. 3642–3647.
[22] U. Mengilli, U. Caliskan, Z. O. Orhan, and V. Patoglu, “Two-port analysis of stability and transparency in series damped elastic actuation,” CoRR, vol. abs/2011.00664, 2021.
[23] U. Mengilli, Z. O. Orhan, U. Caliskan, and V. Patoglu, “Passivity of series damped elastic actuation under velocity-sourced impedance control,” in IEEE World Haptics Conference, 2021.
[24] A. Kamadan, G. Kiziltas, and V. Patoglu, “Co-design strategies for optimal variable stiffness actuation,” IEEE/ASME Transactions on Mechatronics, vol. 22, no. 6, pp. 2768–2779, 2017.
[25] C. H. An and J. Hollerbach, “Dynamic stability issues in force control of manipulators,” in American Control Conference, 1987, pp. 821–827.
[26] S. Eppinger and W. Seering, “Understanding bandwidth limitations in robot force control,” in IEEE ICRA, vol. 4, 1987, pp. 904–909.
[27] W. S. Newman, “Stability and performance limits of interaction controllers,” Journal of Dynamic Systems, Measurement, and Control, vol. 114, no. 4, pp. 563–570, 1992.
[28] G. Pratt and M. Williamson, “Series elastic actuators,” in IEEE IROS, vol. 1, 1995, pp. 399–406.
[29] U. Caliskan and V. Patoglu, “Efficacy of haptic pedal feel compensation on driving with regenerative braking,” IEEE Transactions on Haptics, vol. 13, no. 1, pp. 175–182, 2020.

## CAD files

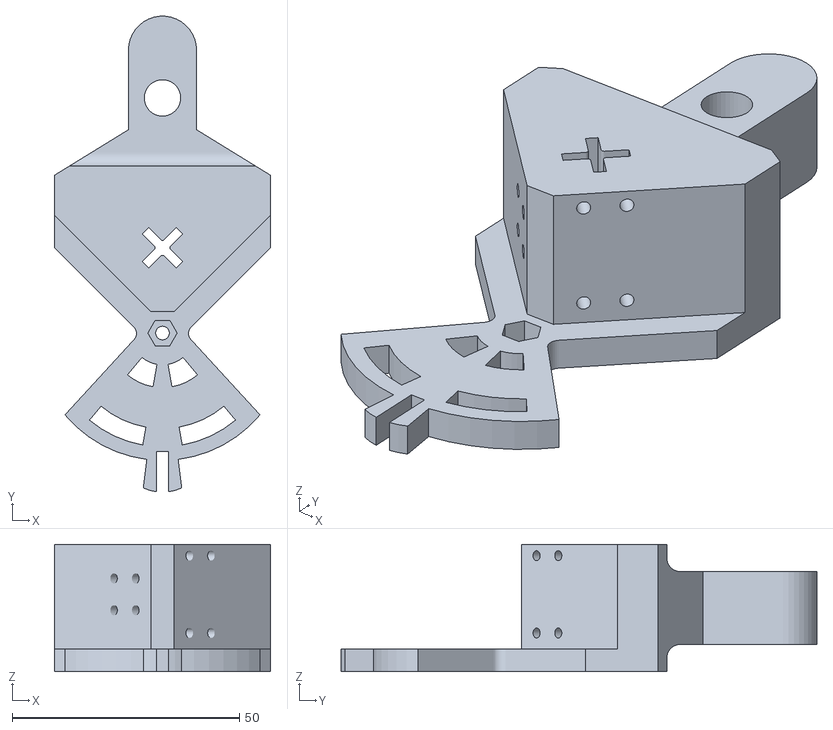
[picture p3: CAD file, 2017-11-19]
CAD/Handle_whole.STL
47.5 x 104.6 x 28.0

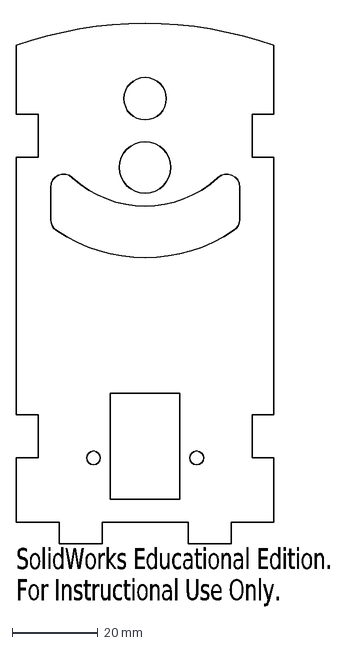
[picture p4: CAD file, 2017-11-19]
CAD/maxon/Base_plexi_face.DXF
SolidWorks Educational Edition.
For Instructional Use Only.

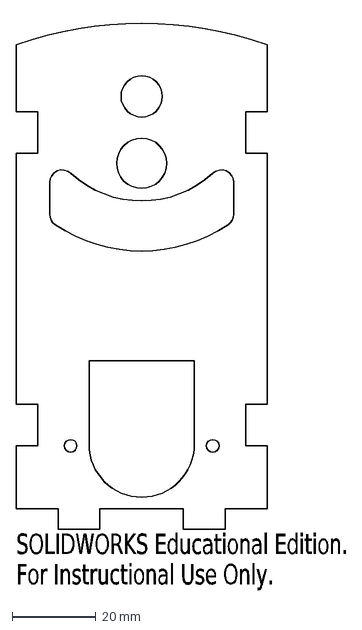
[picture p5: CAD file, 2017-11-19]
CAD/pololu/Base_plexi_face.DXF
SOLIDWORKS Educational Edition.
For Instructional Use Only.

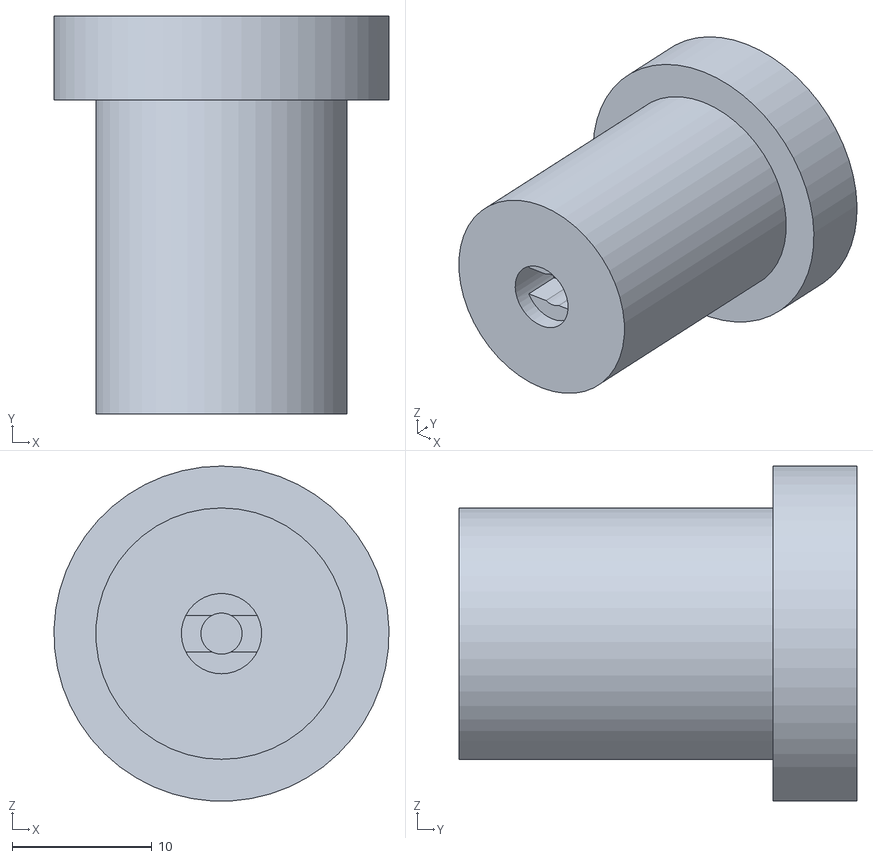
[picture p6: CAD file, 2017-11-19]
CAD/maxon/Pinion.STL
24.0 x 28.5 x 24.0

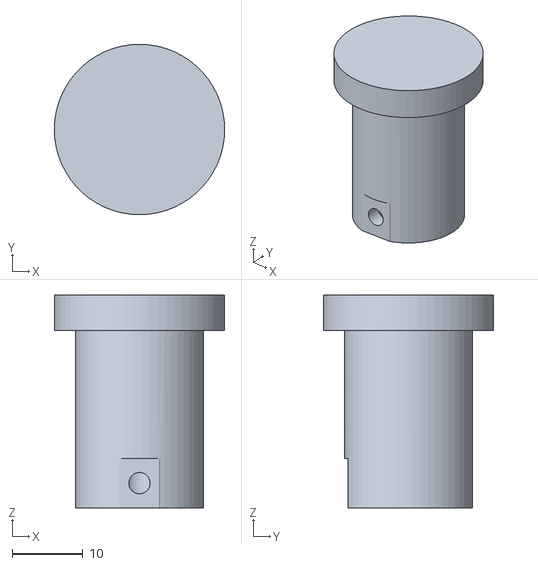
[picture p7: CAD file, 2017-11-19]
CAD/pololu/Pinion.STL
24.0 x 24.0 x 30.0

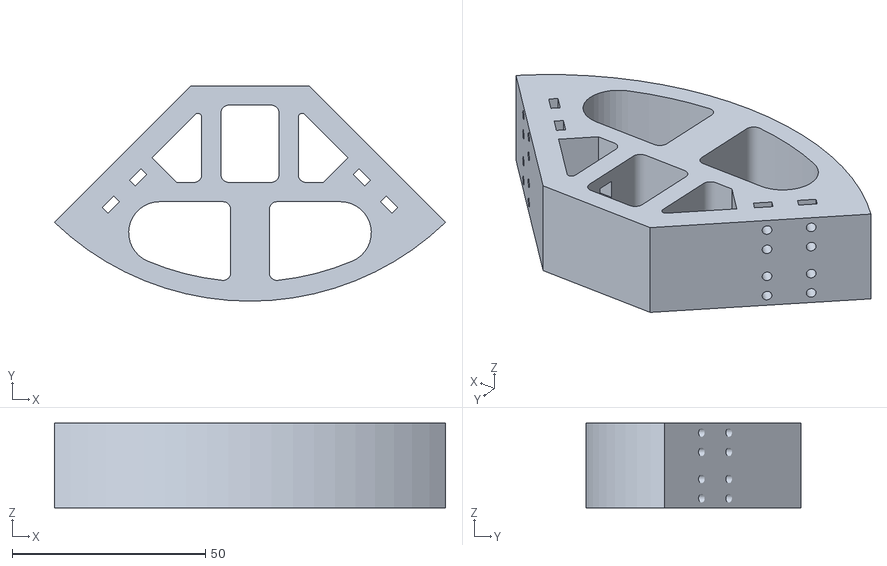
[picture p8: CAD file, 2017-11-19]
CAD/Pulley.STL
101.2 x 55.8 x 22.0

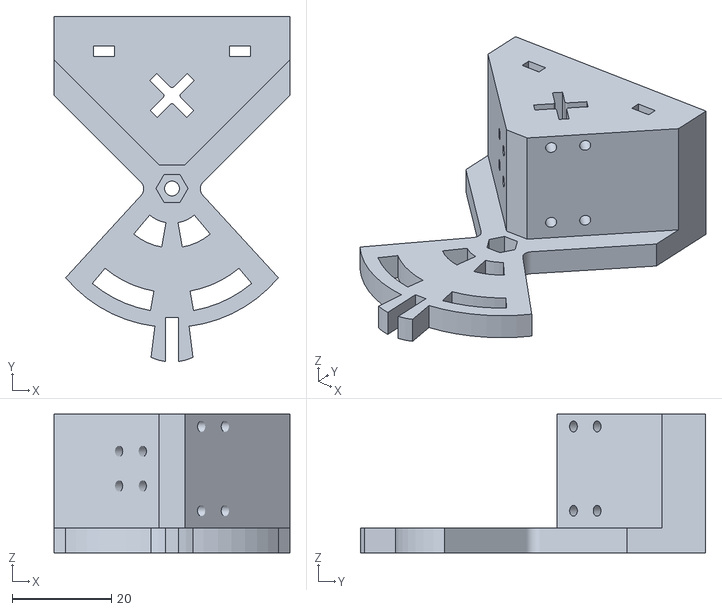
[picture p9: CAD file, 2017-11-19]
CAD/Handle_part1.STL
47.6 x 69.6 x 28.0

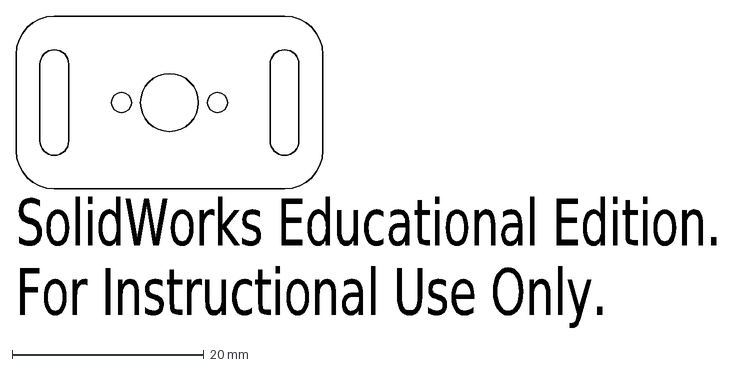
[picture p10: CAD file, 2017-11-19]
CAD/maxon/Motor_holder.DXF
SolidWorks Educational Edition.
For Instructional Use Only.

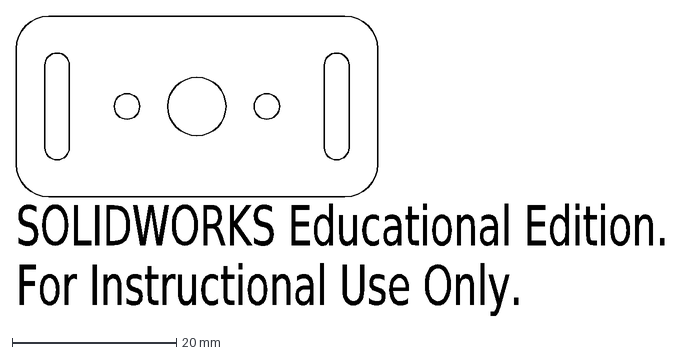
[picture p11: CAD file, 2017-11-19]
CAD/pololu/Motor_holder.DXF
SOLIDWORKS Educational Edition.
For Instructional Use Only.

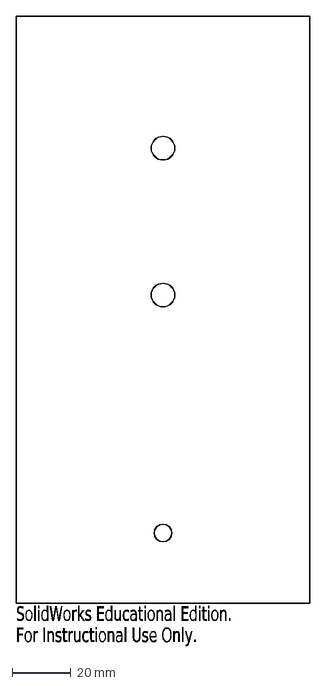
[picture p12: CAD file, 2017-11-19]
CAD/Lower_plate.DXF
SolidWorks Educational Edition.
For Instructional Use Only.

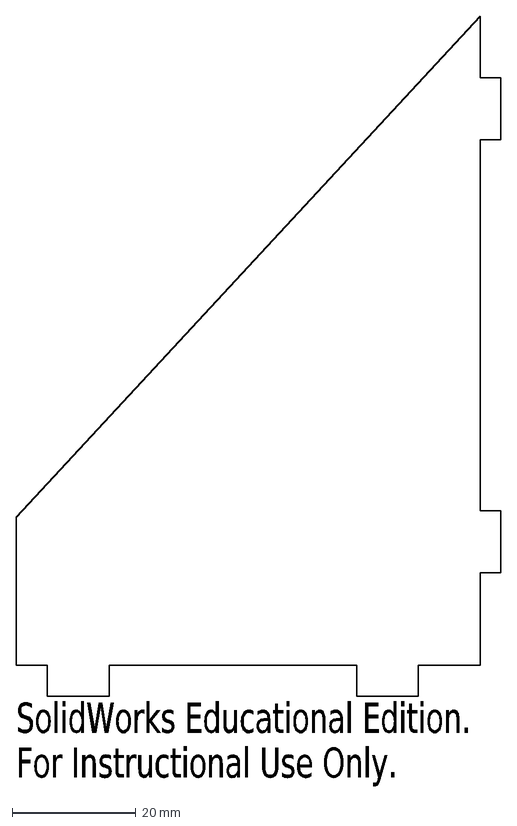
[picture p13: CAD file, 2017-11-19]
CAD/Base_plexi_side.DXF
SolidWorks Educational Edition.
For Instructional Use Only.

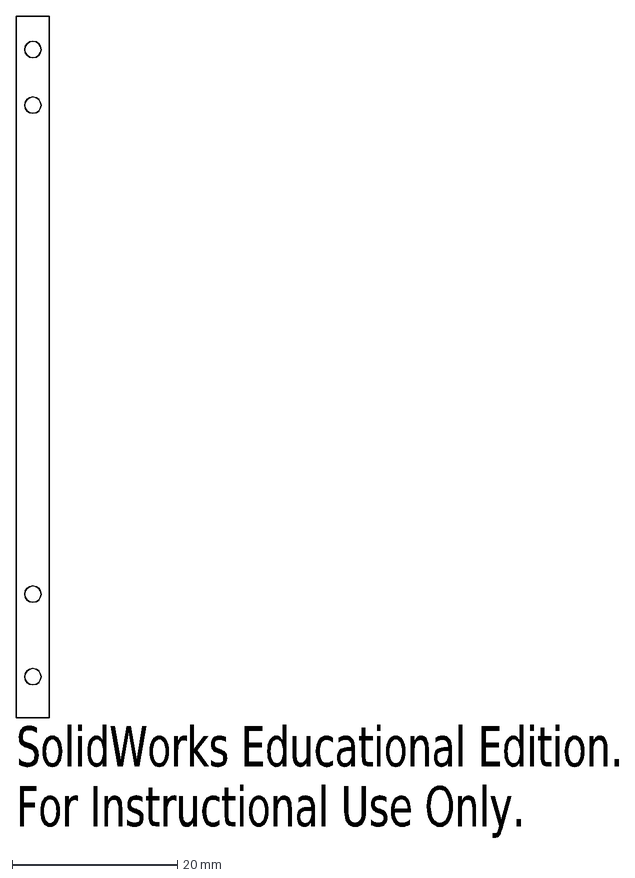
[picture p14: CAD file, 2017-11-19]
CAD/Leaf_spring.DXF
SolidWorks Educational Edition.
For Instructional Use Only.

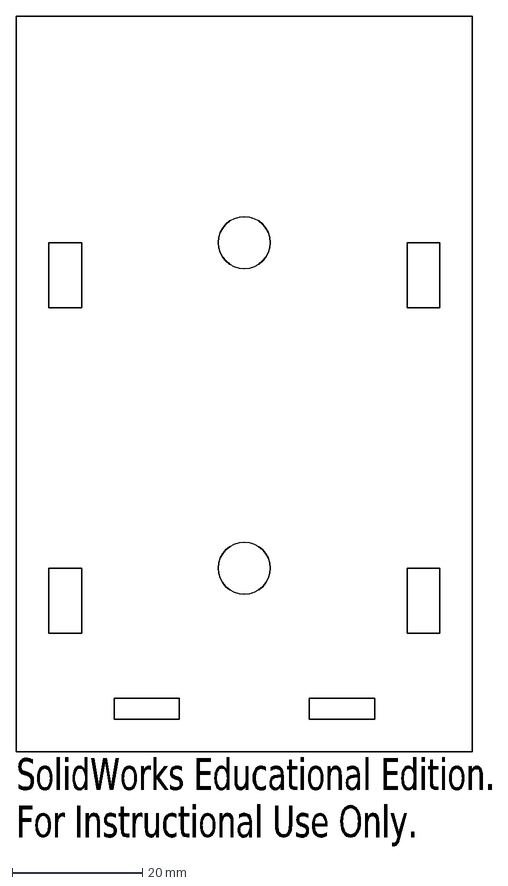
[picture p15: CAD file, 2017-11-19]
CAD/Base_plexi_bottom.DXF
SolidWorks Educational Edition.
For Instructional Use Only.

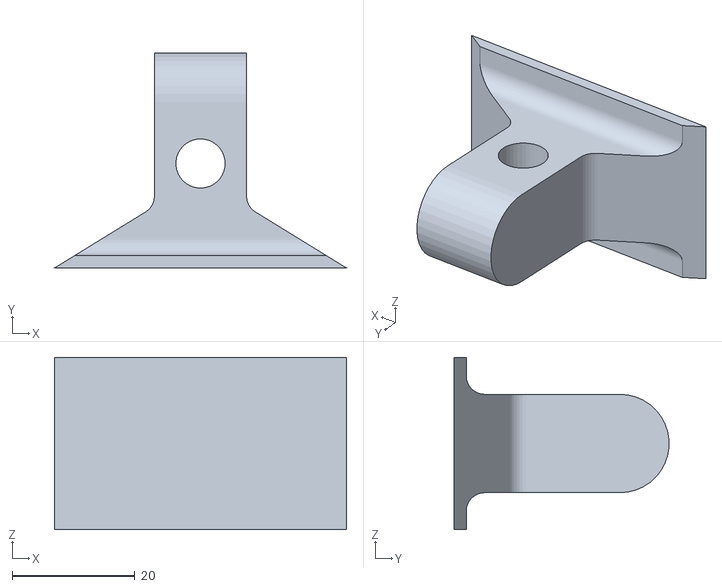
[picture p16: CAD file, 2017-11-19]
CAD/Handle_part2.STL
47.5 x 35.0 x 28.0

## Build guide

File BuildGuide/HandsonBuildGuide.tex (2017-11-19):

\documentclass{beamer}

\usepackage{graphicx}
\usepackage{mwe}

%%%%%%%%%%%%%%%%%%%%%%%%%%%%%%%%%%%%%%%%%%%%%%%%%%%%%%%%%%%%%%%%%%%%%%%%%%%%%%%%
%
%  \zoombox[box line width]{contents}
%
%  optimized version for beamer: in full screen, zoom boxes are centred
%  in the viewer; useable with any documenclass
%
%%%%%%%%%%%%%%%%%%%%%%%%%%%%%%%%%%%%%%%%%%%%%%%%%%%%%%%%%%%%%%%%%%%%%%%%%%%%%%%%
\makeatletter
\newsavebox\zb@x
\newcounter{z@@m}
\usepackage{calc}
\newdimen\B@r\newdimen\P@r
\newdimen\@zw\newdimen\@zh\newdimen\@zd

\newcommand{\zoombox}[2][0]{%
  \leavevmode%
  \sbox\zb@x{#2}%
  \setlength\B@r{1pt*\ratio{\wd\zb@x}{\ht\zb@x+\dp\zb@x}}%
  \setlength\P@r{1pt*\ratio{\paperwidth}{\paperheight}}%
  \ifdim\B@r>\P@r\relax%
    \setlength\@zw{\wd\zb@x}\setlength\@zh{\@zw*\ratio{\paperheight}{\paperwidth}}%
    \setlength\@zd{(\@zh-\ht\zb@x-\dp\zb@x)*\real{0.5}+\dp\zb@x}%
    \setlength\@zh{\@zh-\@zd}%
  \else%
    \setlength\@zh{\ht\zb@x+\dp\zb@x}%
    \setlength\@zw{\@zh*\ratio{\paperwidth}{\paperheight}}%
    \setlength\@zh{\ht\zb@x}\setlength\@zd{\dp\zb@x}%
  \fi%
  \makebox[0pt][l]{\makebox[\wd\zb@x][c]{\makebox[\@zw][l]{%
    \pdfdest name {zbfs\thez@@m} fitr
      width  \@zw\space
      height \@zh\space
      depth  \@zd\space
  }}}%
  \pdfdest name {zb\thez@@m} fitr
    width  \wd\zb@x\space
    height \ht\zb@x\space
    depth  \dp\zb@x\space
  \immediate\pdfannot 
    width  \wd\zb@x\space
    height \ht\zb@x\space
    depth  \dp\zb@x\space
  {%
    /Subtype/Link/H/N
    /Border [0 0 #1 [1 2]]
    /A <<
      /S/JavaScript
      /JS (
        if(typeof(zoomed)=='undefined'||!zoomed){
          var lastView=this.viewState;
          if(app.fs.isFullScreen) this.gotoNamedDest('zbfs\thez@@m');
          else this.gotoNamedDest('zb\thez@@m');
          zoomed=true;
        }else{
          this.viewState=lastView;
          zoomed=false;
        }
      )
    >>
  }%
  \usebox{\zb@x}%
  \stepcounter{z@@m}%
} 
\makeatother
%%%%%%%%%%%%%%%%%%%%%%%%%%%%%%%%%%%%%%%%%%%%%%%%%%%%%%%%%%%%%%%%%%%%%%%%%%%%%%%

\title{HandsOn-SEA Build Guide}  \vspace{25mm}
\date{}

\begin{document}
\setbeamertemplate{caption}{\raggedright\insertcaption\par} %To remove "Figure:" from caption
\begin{frame}[t, plain]
  \vspace{15mm}
  \titlepage
  \vspace{0mm}
*All the pictures placed on the document can be zoomed in an out by click on them. You may need Adobe Acrobat for this functionality. \\
*Selection of different motors can necessitate some minor changes in the designs  of certain parts but they don't affect the manufacturing procedure. 
\end{frame}

\begin{frame}[t]{Assembling the base}
\begin{itemize} 
\item Components
\begin{itemize} \scriptsize
\setlength\itemsep{0.5mm}
\item Plexiglass base (Base)
\item Plexiglass base (Side)
\item Plexiglass base (Face)
\item Bearing
\item Plexiglass base (Lower plate)(Optional)
\item Super glue 
\item Cloroform (Optional)
\end{itemize}

\item Procedure
\begin{enumerate} \scriptsize
\item Glue one of the sides parts and face part together.
\item Glue the other face part to the assembly.
\item Glue the assembly into the plexiglass base.
\item Glue the bearing into the face.
\item Use glue or cloroform to fix the base assembly on the lower plate (Optional)
\end{enumerate}
\end{itemize}
\vspace{-1mm}
\scriptsize End product of this section should look like:
\newline
\zoombox{}
\zoombox{}
\zoombox{}
\end{frame}

\begin{frame}[t]{Assembling the Handle, Pulley and spring steels}
\vspace{-2mm}
\begin{itemize}
\item	Components
\newline
\begin{minipage}{0.4\textwidth} 
\raggedright
\begin{itemize} \scriptsize
\setlength\itemsep{-0.3mm}
\item	3D printed pulley
\item	3D printed handle
\item	4x spring steels
\item Hall effect sensor
\item 3 pin single row pin header
\end{itemize}
\end{minipage}
\begin{minipage}{0.5\textwidth}
\begin{itemize} \scriptsize
\setlength\itemsep{-0.5mm}
\item 8x screws(D:2 mm, L: 15mm)
\item 8x screws(D:2 mm, L: 10mm)
\item 16x 2mm nuts and washers
\item Screw driver
\item Tooth pick
\item Positioning base
\end{itemize}
\end{minipage}
\vspace{1mm}
\item Procedure 
\begin{enumerate} \scriptsize
\item First take out the metal pieces and then glue the 3 pin female header on the handle.
\item Mount the hall effect sensor into the handle.
\zoombox{}
\item Solder the legs of the hall effect sensor with cables, use heat shrink tubes and hot glue gun to protect the legs. 
\item Mount the cube magnets into the pulley with each magnet facing the same pole towards each other
\zoombox{}
\zoombox{}
\item Screw in the metal strips on the handle part. Using a toothpick and positioning base is very handy for alligning the screws with nuts. 
\zoombox{}
\zoombox{}
\item Screw in the metal strips on the pulley part.
\zoombox{}
\end{enumerate}
\end{itemize}
\scriptsize
The end product of this section should look like:
\zoombox{}
\newline
Note: This is the only time consuming part of the assembly. 
\end{frame}

\begin{frame}[t]{Mounting the motor and top}
\begin{itemize} 
\vspace{-4mm}
\item Components
\newline
\begin{minipage}{0.4\textwidth}
\begin{itemize} \scriptsize
\setlength\itemsep{-0.3mm}
\item Motor
\item Pinion
\item Motor holder
\item Shoulder screw
\item 3 mm thick PVC table cover
\end{itemize}
\end{minipage}
\begin{minipage}{0.5\textwidth}
\begin{itemize} \scriptsize
\setlength\itemsep{-0.5mm}
\item 3mm washer
\item 2x D:2 L:5 mm screws 
\item Heat shrink tube (wider than pinion)
\item Hot air gun
\end{itemize}
\end{minipage}
\item Procedure
\begin{enumerate} \scriptsize
\item Cut a piece of PVC table protector and paste it along the circumference of the pulley part as it is shown in the figure. The width of the PVC strip that we use is 15 mm but this can vary. The thickness can also vary. 
\item Use the shoulder screw and a washer to screw the handle part to the face through the bearing.
\zoombox{}
\zoombox{}
\item Screw the motor holder on the motor.
\zoombox{}
\item Using a hot air gun wind a heat shrink tube around the pinion to avoid slip. Pinion's tip has a greater radius for restraining the pulley from tilting forwards during operation.
\zoombox{}
\item Place the pinion on the shaft of the motor. If this assembly is not tight enough the pinion can fall during the operation. 
\zoombox{}
\item Screw the motor holder on the base. The motor holder should be in front of the face.
\zoombox{}
\item The height adjustment of the motor should calibrated. Pinion should exert just enough force on pulley to provide desired friction.
\end{enumerate}
\end{itemize}
\scriptsize
\vspace{-2mm}
The end product of this section should look like
\hspace{2mm}
\zoombox{}
\end{frame}

\begin{frame}[t]{Creating the PCB}
\begin{itemize} 
\item Components
\begin{itemize} \scriptsize
\item Pressed/Printed Circuit Board
\item 2x Resistors
\item DRV 8801 Driver
\item Benchtop drill press
\item 3 pin PCB connector
\item 4 pin PCB connector
\item Single and double row 1" female pin headers
\end{itemize}
\item Procedure
\begin{enumerate} \scriptsize
\item Using the Eagle files press the raw circuit board
\zoombox{}
\item Drill through the required holes
\zoombox{} (Note that the when printed the apperance is reflected around vertical axis)
\item First solder the legs (male pin headers) of DRV8801 on the PCB, then solder the DRV8801.
\item Selection of resistors for the voltage to drop the voltage from 0-5V to 0-≤3.3 V range.  1.5 and 2.7(green one) kOhm were used but can vary. Make sure the resistance values are high enough though.
\item Place in and solder the other required components as seen in the pictures. 
\zoombox{}
\zoombox{}
\end{enumerate}
\end{itemize}
\end{frame}

\begin{frame}[t]{Electronic Assembly}
\begin{itemize} 
\item Components
\begin{itemize} \scriptsize
\item PCB
\item TI F28069M Microcontroller
\item HandsOn SEA mechanical assembly
\item Jumper wires
\item 24 V power supply
\item Screw driver
\end{itemize}
\item Procedure (please refer to the pictures for each step)
\begin{enumerate} \scriptsize
\item Place the PCB on the microcontroller
\zoombox{}
\zoombox{}
\item Connect the hall effect sensor to 3 pin PCB connector
\zoombox{}
\item Plug in 6 male ends of female to male jumper wires on the motor's connector. Using different type of motor would of course change this step. 
\zoombox{}
\item Connect the power supply wires and the motor energy supply wires to 4 pin PCB connector.
\zoombox{}
\item Plug in both PCB connectors and place the PCB on the microcontroller
\item Plug in the quadrature encoder wires (GND, 5V, A, B) to their corresponding positions on the microcontroller 
\zoombox{}
\end{enumerate}
The end product of this section should look like 
\zoombox{}

\end{itemize}
\end{frame}

\end{document}

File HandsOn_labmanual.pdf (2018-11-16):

ME 403

Introduction to Robotics

# Laboratory Modules

# Fall 2016

These laboratory exercises are grouped into 6 modules and aim to demonstrate the concept of sensor-actuator non-collocation for motion and force controlled robotic systems. Furthermore, the students will be exposed to force control, impedance control and series elastic actuation through these laboratory exercises.

## A Single DoF Educational Robot with Series Elastic Actuation

HandsOn-SEA¹² is a single DoF admittance type robot featuring series elastic actuation. The device features a built-in force sensing unit that estimates the force applied on the handle by measuring the deflection of a compliant cross flexure pivot intentionally placed between the handle and the pulley. A geared DC motor actuates the pulley-handle module through a friction drive transmission. Figure 1 presents the main design features of HandsOn-SEA.

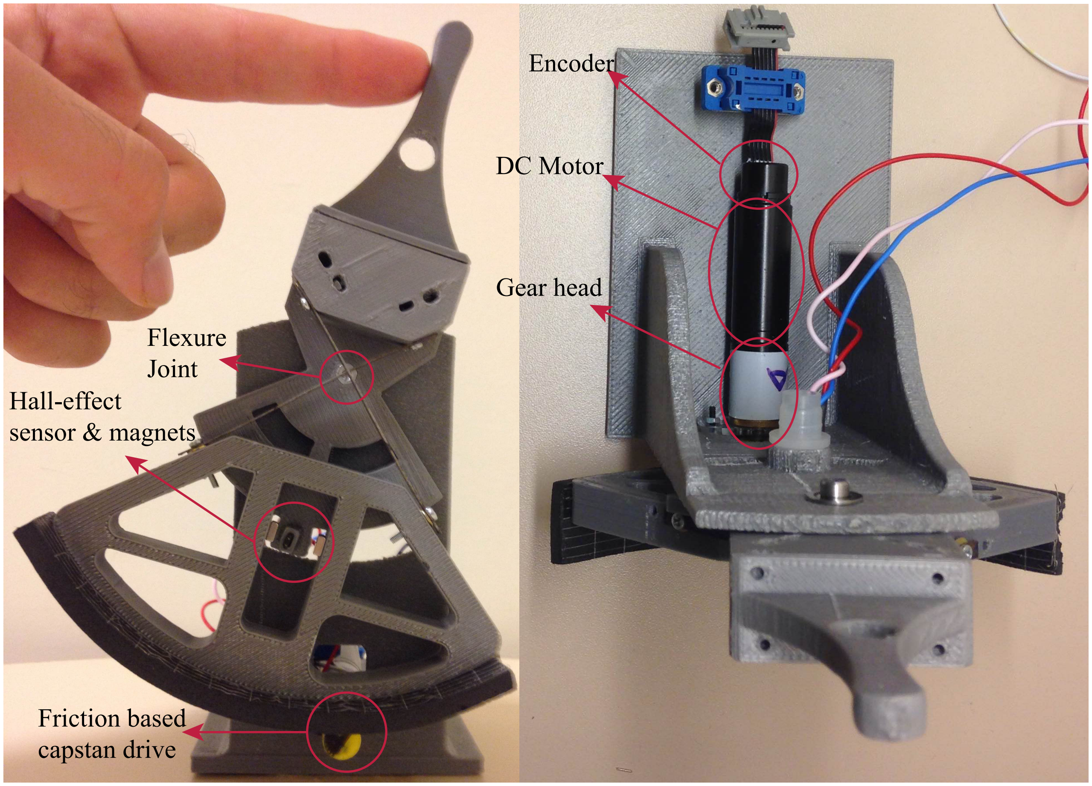
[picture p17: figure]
Flexure Joint; Friction based capstan drive; Hall-effect sensor & magnets; Encoder; DC Motor; Gear head

Figure 1: HandsOn-SEA—A single DoF educational robot with series elastic actuation

1Ata Otaran, Ozan Tokatli, and Volkan Patoglu, Hands-On Learning with a Series Elastic Educational Robot, Springer, Lecture Notes in Computer Science, 2016.
2Ata Otaran, Ozan Tokatli, and Volkan Patoglu, HandsOn-SEA: A Series Elastic Educational Robot for Physical Human Robot Interaction, IEEE Transactions on Haptics, (in review).
ME 403 - Introduction to Robotics | Page 1 of 8

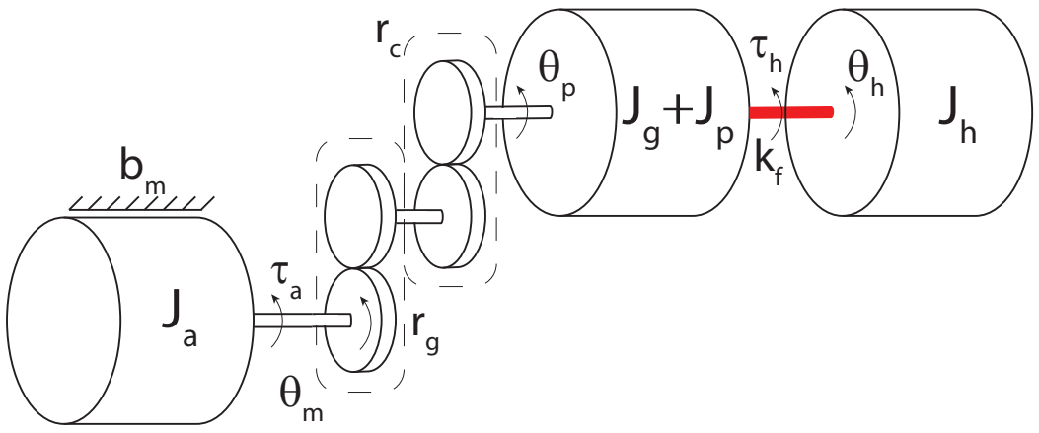
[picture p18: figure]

Figure 2: Schematic model HandsOn-SEA

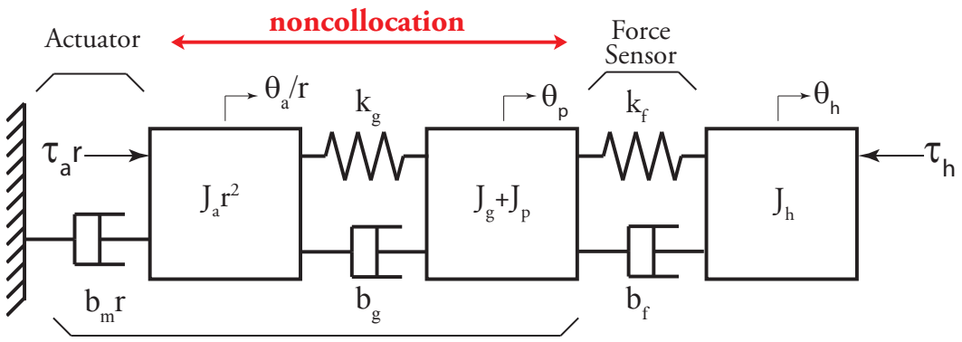
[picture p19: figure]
Force Sensor Actuator θ a; noncollocation

# Robot

Figure 3: A linear analog of the system model that also captures the sensor-actuator non-collocation. Here kg and bg and the inertia distribution between Ja and Jg is an approximate model to capture the effect of first vibration mode of the system. Symbols kf , bf signify the force sensor attached to the handle that interacts with the environment. Inertia of the handle is assumed to be negligible.

Table 1: Parameters of HandsOn-SEA
Ja – inertia of the motor | 1.3 | gr-cm²
Jg – inertia of the gearhead | 0.05 | gr-cm²
Jh – inertia of the handle about the bearing | 1.93 | gr-cm²
Jp – inertia of the sector pulley about the bearing | 14.7 | gr-cm²
rg – gearhead reduction ratio | 84:1
rc – capstan reduction ratio | 73:9
kf – stiffness of the cross flexure pivot | 5000 | N-mm/rad
L – motor inductance | 0.452 | mH
R – motor resistance | 10.7 | Ohm
bm – cumulative damping of the motor | 0.025 | N-mm/s
Km – motor torque constant | 16.2 | mN-m/A
Kb – motor back-emf constant | 61.7 | rad/sec/V
τm – mechanical time constant | 5.31 | ms

## Module 1

This module is designed to implement motion controllers for and to analyse/experience stability limits of a single DoF motion controlled rigid-body dynamic system.

Pre-Lab Exercises

Please solve the pre-lab exercises 1–6 before attending the lab and prepare a report that presents your work. Your reports will be collected at the beginning of the laboratory session. It is recommended that you keep a copy of your report for yourself.

1 Review what a Bode plot is and learn the significance of the -3 dB magnitude level.

2 Use the data in the file Bode example.m in SUCourse to draw a Bode gain plot in Matlab. Note that the axes of your plot should be logarithmic.

3 Symbolically derive the transfer function between the motor voltage V input and the motor armature position θa output of HandsOn-SEA. The substitute the parameters listed in Table 1 to your transfer function. For this analysis, assume kg is infinitely stiff and reflect the inertia of the gearbox and the pulley to the motor side by multiplying by the square of the appropriate gear ratios.

Spong book Chapters 6.1–6.2 and the following web site may be useful during your derivations: http: // ctms. engin. umich. edu/ CTMS/ index. php? example= MotorPosition& section= SystemModeling (http://ctms.engin.umich.edu/CTMS/index.php?example=MotorPosition&section=SystemModeling)

4 Verify that the electrical time constant L/R is much smaller than the mechanical time constant Ja/bm for the DC motor. Set L/R to zero in order to reduce the previously derived transfer function to a second order one. Compare the step response of the reduced order transfer function to the original one and comment on the difference.

5 Calculate the closed loop transfer function when the position of the motor armature θa is regulated using a proportional position controller. Draw the root locus plot for this system and comment on how closed loop pole positions are affected as the proportional control gain is increased. According to this analysis, can the system become unstable?

6 Calculate gains for a PD position controller such that the closed loop system possesses critical damping and has a bandwidth of ω = 15 rad/s.

Laboratory Exercises

Please solve the exercises 1–2 during the lab and prepare a report that presents your work. Your reports will be collected at the end of the laboratory session.

1 Implement a PD position controller for the DC motor of the device. Try the PD controller gains that you have calculated analytically for the pre-lab exercise. Tune these gains empirically until you get the fastest non-overshooting stable step response.

2 Study the root-locus plot of the closed loop transfer function of the motion control system you derived as a part of the pre-lab exercises. Discuss possible reasons of the stability limits you experience during the physical implementation of the controller.

3 Using the sample files provided in SUCourse, collect data with the tuned gains to draw Bode plots of the system and determine the closed-loop position control bandwidth of the device.

## Module 2

This module is designed to demonstrate the inherent stability limits of closed-loop control systems that possess sensor-actuator non-collocation, as modelled in Figure 3.

Pre-Lab Exercises

Please solve the pre-lab exercises 1–4 before attending the lab and prepare a report that presents your work. Your reports will be collected at the beginning of the laboratory session. It is recommended that you keep a copy of your report for yourself.

1 Read Sections 7.5–7.6.1(6.5–6.6.1 in some editions), starting with Drive Train Dynamics - from the Spong book. Given the system model in Figure 3, symbolically derive the following transfer functions to capture the effect of joint flexibility: i) Motor torque Tact is the input and the motor armature position θa is the output, and ii) motor torque Tact is the input and the pulley position θp is the output. During these calculations, you can neglect kf and bf as the system is not interacting with the environment.

2 As a crude approximation of the system, substitute the following parameters to form numerical transfer functions: J1 = Ja, b1 = kb ∗ km/R, J2 = Jg + Jp/(rg ∗ rp)

2
, b2 = bm, and k2 = 4000/rg Nm/rad.

Plot two root locus graphs for proportional (PD) controlled system when the position of the motor armature θa and scaled position of the pulley θp ∗ (rc ∗ rp) are fed back, respectively.

Comment on the stability and performance of both control architectures as the controller gain is increased. Note that the goal of feedback is to control the position of the pulley θp for both architectures.

3 Derive the transfer function between the motor torque Tact and the torque estimated by the torque sensor (Tsens = kf ∗(θp−θh))for the system in Figure 3, when the handle is fixed to a rigid environment. Let kf = 5000 Nmm/rad, bf = 0 and plot root locus graph for proportional (P) controlled system when Tsens is fed back. Comment on the stability and performance of of this explicit force control system as the controller gain is increased.

4 Identify the causes of sensor-actuator non-collocation for force controlled system and discuss why explicit force control systems inherently possess sensor actuator non-collocation.

Laboratory Exercises

Please solve the exercises 1–2 during the lab and prepare a report that presents your work. Your reports will be collected at the end of the laboratory session.

1 Implement a PI explicit force controller based on the force estimations acquired through the deflections of the cross flexure pivot.

2 Starting with low force control gains, empirically tune your controller gains for aggressive but stable response with no chatter. Note the gain level when contact becomes unstable, that is, chatter is observed. Compare this gain with the stability limit of the position controller when link position is fed back. Comment on the relationship between magnitude of these two controller gains.

## Module 3

This module is designed to provide an intuitive understanding of the inherent trade-off between the sensor stiffness and the force controller gain.

Pre-Lab Exercises

Please solve the pre-lab exercises 1–3 before attending the lab and prepare a report that presents your work. Your reports will be collected at the beginning of the laboratory session. It is recommended that you keep a copy of your report for yourself.

1 Use the following formula for calculating the effective stiffness kf c of the cross flexure joint of HandsOn-SEA. The relevant geometric/material properties are listed in Table 2.

kf c =

8EI(1 − 3λ + 3λ

2
)cosα
lLh
N/rad | (1)

Table 2: Parameters characterizing the cross flexure joint
Parameter | Value | Unit
Thickness Width Length Pivot ratio Pivot angle Young’s modulus Second moment of area Distance between center of rotation and handle | t = 1 w = 4 l = 59.33 λ = 0.68 2α = 90 E = 2*10⁵ I = w*t³ Lh=62 | mm mm mm -◦ N/mm² mm⁴ mm

2 Repeat Pre-Lab Exercise 3 of Module 2 by replacing kf with the stiffness kf c of the cross flexure pivot. Compare the controller gains at the limit of stability.

3 Comment on effect of sensor stiffness on stability of explicit force control. Identify and list the advantages and disadvantages of using a more compliant force sensor in terms os stability and performance of the force controlled system.

Laboratory Exercises

Please solve the exercises 1–2 during the lab and prepare a report that presents your work. Your reports will be collected at the end of the laboratory session.

1 Implement PI explicit force controllers with two cross flexure pivots with different levels of compliance. Experimentally determine the highest stable explicit force controller gain that can be implemented for each level of compliance. Observe that the more the force sensor compliance is increased, the more the force controller gains can be increased without inducing instability or chatter.

2 Given that stability limit is directly proportional to the controller gain and sensor stiffness, estimate the stiffness of the new cross flexure pivot based on your experimental data. Compare this value with the analytical stiffness model of this compliant joint.

## Module 4

This module is designed to introduce the concept of series elastic actuation and to provide hands-on experience with SEA by demonstrating the mechanical low-pass filtering behavior and low control bandwidth of these systems.

Series Elastic Actuation (SEA)

The underlying idea of SEA is the reallocation of limited loop gain of the system with non-collocated sensor-actuator, to decrease the force sensor stiffness (by a few orders of magnitude), such that the force controller gain can be increased (by a few orders of magnitude). More aggressive force-feedback controller gains are preferred to achieve fast response times and good robustness properties to compensate for hard-to-model parasitic effects, such as friction and backlash.

While SEA can improve force control performance, this improvement comes with the cost of decreased system control bandwidth. In particular, the introduction of the compliant sensing element significantly lowers bandwidth of the resulting force controlled system.

The advantages of SEA include high active backdrivability within the force control bandwidth and low output impedance for the frequencies over the control bandwidth, due to inherent compliance of the force sensing element. Furthermore, the compliant force sensor acts as a mechanical low pass filter for the system against impacts, impulsive loads and high frequency disturbances, such as torque ripple.

Pre-Lab Exercises

Please solve the pre-lab exercises 1–2 before attending the lab and prepare a report that presents your work. Your reports will be collected at the beginning of the laboratory session. It is recommended that you keep a copy of your report for yourself.

1 When the actuator is locked (is not fast enough to react), HandsOn-SEA behaves like a mass-spring system with Jh and kf c, if the neglect the contribution of kg, which is designed to be orders of magnitude stiffer than kf c. Plot the Bode plot of the Jh-kf c mass-spring system, observe the low pass filtering behaviour that dominates the system dynamics for high frequency inputs, and determine the open-loop bandwidth of the system.

2 The output impedance Zout(s) is characterized by the transfer function when the velocity of the handle sθh(s) is the input and the torque at the handle Tsens(s) is the output. Symbolically calculate this transfer function and substitute in system parameters. Draw the associated Bode plots of Zout(s) and comment on how the output impedance behaves at low and high frequencies. Compare the output impedance at high frequencies with the Bode plot of the previous question and comment on the similarities.

Laboratory Exercises

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

1 Implement an actively backdrivable system by setting the desired force in your explicit force controller to zero. Apply low, medium and high frequency inputs to the handle of device with your hand. Repeat the same process when the controller is off. Comment on how the output impedance changes with the gradual increase in frequency for both cases.

2 Apply high frequency torque ripples through the motor while holding the handle. Discuss how this torque ripple is transferred to the handle. Plot the data collected by force sensor during this input and compare it along with the torque ripple input. Comment on the low pass filtering due to motor dynamics and due to compliant sensor.

## Module 5

This module is designed to introduce the cascaded controller architecture for SEA and to evaluate the force tracking performance of the device under cascaded control. The cascaded control architecture for SEA is depicted in Figure 4. This controller consists of an inner velocity control loop, an intermediate force control loop and an outer impedance control loop.

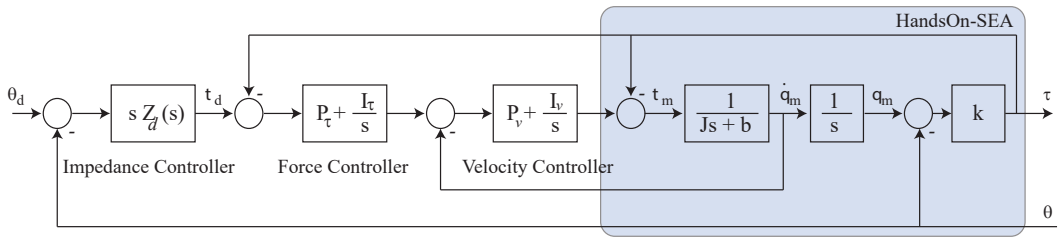
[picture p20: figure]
Impedance Controller; Force Controller; Velocity Controller; HandsOn-SEA

Figure 4: Cascaded controller

The inner loop of the control structure employs a robust motion controller to compensate for the imperfections of the power transmission system, such as friction, stiction and slip, rendering the motion controlled system into an ideal velocity source within its control bandwidth. The intermediate control loop incorporates force feedback into the control architecture and ensures good force tracking performance under adequately designed inner loop. Finally, the outer loop determines the effective output impedance of the system within the system control bandwidth.

Pre-Lab Exercises

Please solve the pre-lab exercises 1–2 before attending the lab and prepare a report that presents your work. Your reports will be collected at the beginning of the laboratory session. It is recommended that you keep a copy of your report for yourself.

1 Using the template provided in SUCourse and form a Simulink model of the cascaded loop controller
for HandsOn-SEA.

2 Study Impedance Control in Chapter 9.3.2 of the Spong book. Explain the virtual dynamics the cascaded impedance controller is designed render. Discuss how the inertia of the handle (which is located after the force sensor) affects the rendering performance.

Laboratory Exercises

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

1 Compare the Simulink file you have created with the one provided in the lab. Update your model and note the differences.

2 Use the provided Simulink models for control and the associated .m files for visualization of the following experiments:

– Backdrivability: Desired impedance is set to zero such that the system tries to achieve ideal backdrivability. Increase the force controller gain until instability is observed.
– Rendering a Virtual Wall: Desired impedance is set to a stiff spring with some damping to render virtual wall. Note that the virtual wall rendering implements a unidirectional constraint such that the system is free to move with high backdriveability when operating outside the virtual wall, while the controller pushes the user outside acting as a spring when the virtual wall constraint is violated. Increase the stiffness and damping of the virtual wall by changing the gains of the desired impedance block. Discuss the effect of virtual stiffness and damping on the stability of rendering.
– Rendering a Mass-Spring-Damper : Desired impedance is set to a mass-spring-damper system with second order dynamics. Calculate the natural frequency of the virtual mass-spring-damper system and note that the virtual system has a resonance at this frequency. Excite the system at frequencies lower and higher than this natural frequency and discuss the system response.

## Module 6

This module is designed to demonstrate the bandwidth limitation of SEA by characterizing the small, medium and high force bandwidth of HandsOn-SEA as in Figur 5.

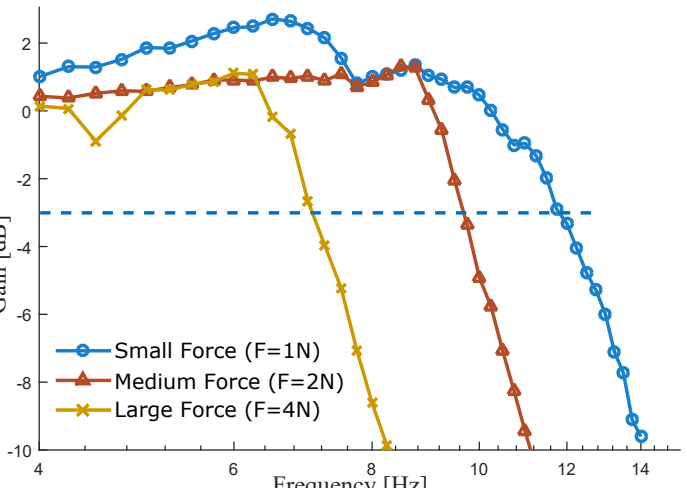
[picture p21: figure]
Small Force (F=1N) Medium Force (F=2N) Large Force (F=4N)

## Frequency [Hz]

## Gain [dB]

Figure 5: A sample Bode magnitude plot characterizing closed-loop small, medium, and high force bandwidths

Pre-Lab Exercise

You are not required to submit a report for this pre-lab.

1 Watch the lower video at http://hmi.sabanciuniv.edu/?page_id=992 that demonstrates how to perform the force bandwidth experiments.

2 Download the relevant files from SUCourse and study the instructions on how to use them.

Laboratory Exercises

Please solve the exercises 1–4 during the lab and prepare a report that presents your work. Your reports will be collected at the end of the laboratory session.

1 Characterize the low force control bandwidth of HandsOn-SEA. Provide a copy of your Bode magnitude plot in your lab report. Compare this bandwidth with the position control bandwidth you have characterized in Module 1.

2 Characterize the medium force control bandwidth of HandsOn-SEA. Provide a copy of your Bode magnitude plot in your lab report. Compare this bandwidth with the low force control bandwidth you have characterized in the previous exercise and report the percent decrease.

3 Characterize the large force control bandwidth of HandsOn-SEA. Provide a copy of your Bode magnitude plot in your lab report. Compare this bandwidth with the low force control bandwidth you have characterized in the first exercise and report the percent decrease.

4 Discuss the underlying reasons for the decrease in force control bandwidth of SEA as the reference force magnitude gets larger.

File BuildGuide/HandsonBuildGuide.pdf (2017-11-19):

# HandsOn-SEA Build Guide

## *All the pictures placed on the document can be zoomed in an out by click on them. You may need Adobe Acrobat for this

functionality.

## *Selection of different motors can necessitate some minor changes in the designs of certain parts but they don’t affect the

manufacturing procedure.

# Assembling the base

## I Components

I Plexiglass base (Base)
I Plexiglass base (Side)
I Plexiglass base (Face)
I Bearing
I Plexiglass base (Lower plate)(Optional) I Super glue
I Cloroform (Optional)

## I Procedure

1. Glue one of the sides parts and face part together.
2. Glue the other face part to the assembly.
3. Glue the assembly into the plexiglass base.
4. Glue the bearing into the face.
5. Use glue or cloroform to fix the base assembly on the lower plate (Optional)

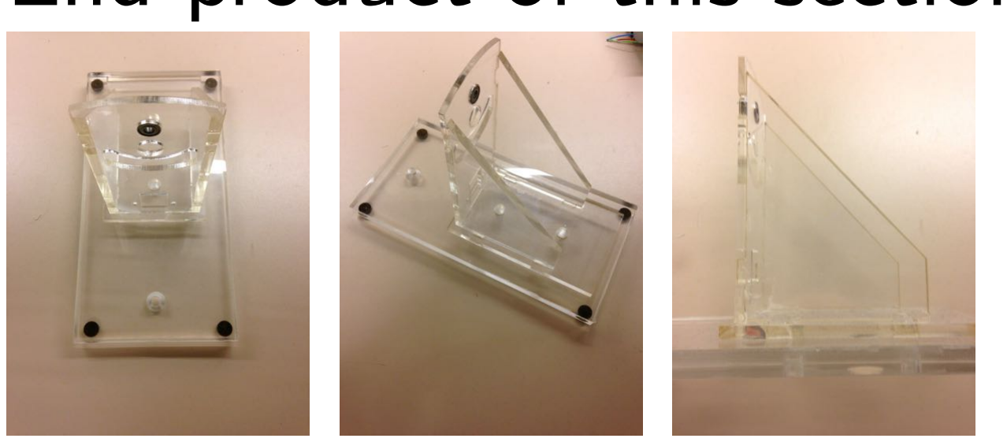
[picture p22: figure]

End product of this section should look like:

# Assembling the Handle, Pulley and spring steels

## I Components

I 3D printed pulley
I 3D printed handle
I 4x spring steels
I Hall effect sensor
I 3 pin single row pin header

I 8x screws(D:2 mm, L: 15mm) I 8x screws(D:2 mm, L: 10mm) I 16x 2mm nuts and washers I Screw driver
I Tooth pick
I Positioning base

## I Procedure

1. First take out the metal pieces and then glue the 3 pin female header on the handle.
2. Mount the hall effect sensor into the handle.
3. Solder the legs of the hall effect sensor with cables, use heat shrink tubes and hot glue gun to protect the legs.
4. Mount the cube magnets into the pulley with each magnet facing the

same pole towards each other
5. Screw in the metal strips on the handle part. Using a toothpick and

positioning base is very handy for alligning the screws with nuts.

6. Screw in the metal strips on the pulley part.

The end product of this section should look like:
Note: This is the only time consuming part of the assembly.

# Mounting the motor and top

## I Components

I Motor
I Pinion
I Motor holder
I Shoulder screw
I 3 mm thick PVC table cover

I 3mm washer
I 2x D:2 L:5 mm screws
I Heat shrink tube (wider than pinion) I Hot air gun

## I Procedure

1. Cut a piece of PVC table protector and paste it along the circumference of the pulley part as it is shown in the figure. The width of the PVC strip that we use is 15 mm but this can vary. The thickness can also vary.
2. Use the shoulder screw and a washer to screw the handle part to the face

through the bearing.

3. Screw the motor holder on the motor.
4. Using a hot air gun wind a heat shrink tube around the pinion to avoid slip. Pinion’s tip has a greater radius for restraining the pulley from tilting forwards during operation.
5. Place the pinion on the shaft of the motor. If this assembly is not tight

enough the pinion can fall during the operation.
6. Screw the motor holder on the base. The motor holder should be in front of the face.
7. The height adjustment of the motor should calibrated. Pinion should exert just enough force on pulley to provide desired friction.
The end product of this section should look like

# Creating the PCB

## I Components

I Pressed/Printed Circuit Board I 2x Resistors
I DRV 8801 Driver
I Benchtop drill press
I 3 pin PCB connector
I 4 pin PCB connector
I Single and double row 1” female pin headers

## I Procedure

1. Using the Eagle files press the raw circuit board
2. Drill through the required holes (Note that the when printed the apperance is reflected around vertical axis)
3. First solder the legs (male pin headers) of DRV8801 on the PCB, then solder the DRV8801.
4. Selection of resistors for the voltage to drop the voltage from 0-5V to 0-3.3 V range. 1.5 and 2.7(green one) kOhm were used but can vary. Make sure the resistance values are high enough though.
5. Place in and solder the other required components as seen in the pictures.

# Electronic Assembly

## I Components

I PCB
I TI F28069M Microcontroller
I HandsOn SEA mechanical assembly I Jumper wires
I 24 V power supply
I Screw driver

## I Procedure (please refer to the pictures for each step)

1. Place the PCB on the microcontroller
2. Connect the hall effect sensor to 3 pin PCB connector
3. Plug in 6 male ends of female to male jumper wires on the motor’s connector. Using different type of motor would of course change this step.
4. Connect the power supply wires and the motor energy supply wires to 4

pin PCB connector.
5. Plug in both PCB connectors and place the PCB on the microcontroller
6. Plug in the quadrature encoder wires (GND, 5V, A, B) to their

corresponding positions on the microcontroller

## The end product of this section should look like

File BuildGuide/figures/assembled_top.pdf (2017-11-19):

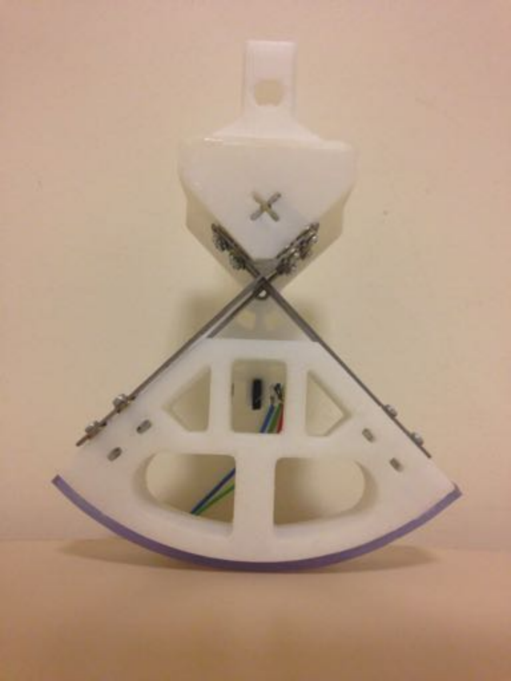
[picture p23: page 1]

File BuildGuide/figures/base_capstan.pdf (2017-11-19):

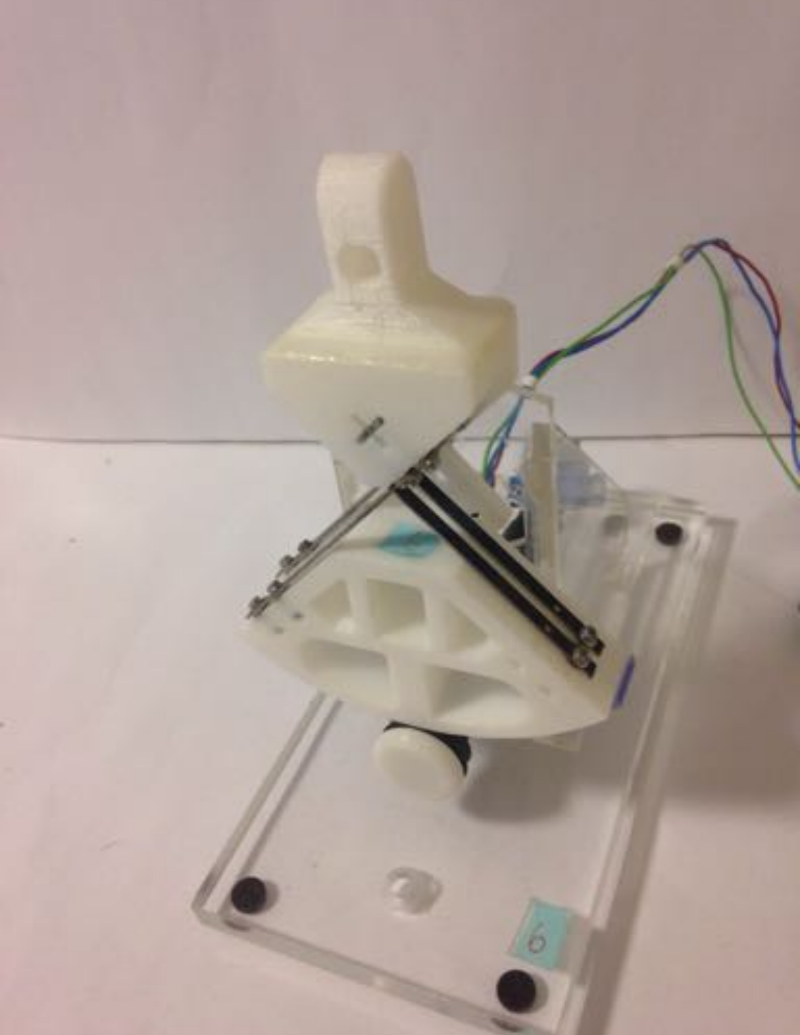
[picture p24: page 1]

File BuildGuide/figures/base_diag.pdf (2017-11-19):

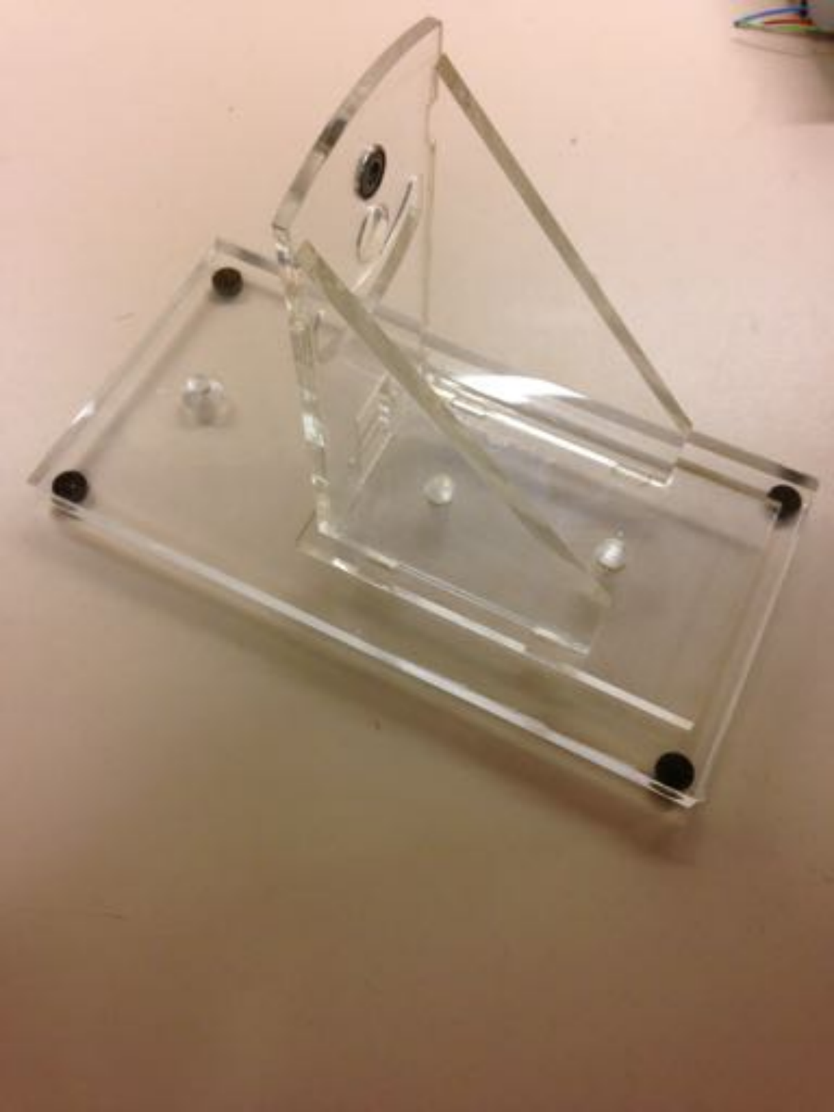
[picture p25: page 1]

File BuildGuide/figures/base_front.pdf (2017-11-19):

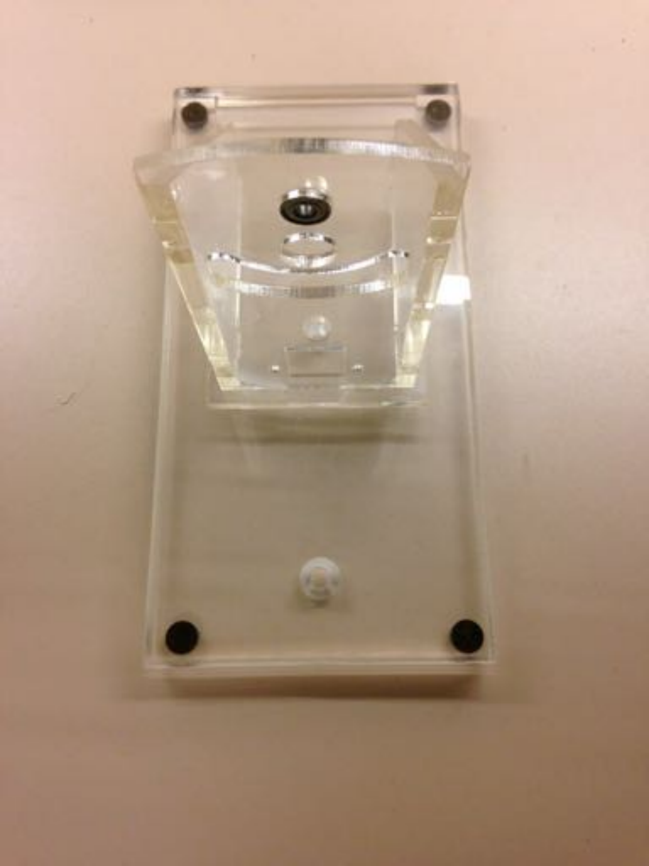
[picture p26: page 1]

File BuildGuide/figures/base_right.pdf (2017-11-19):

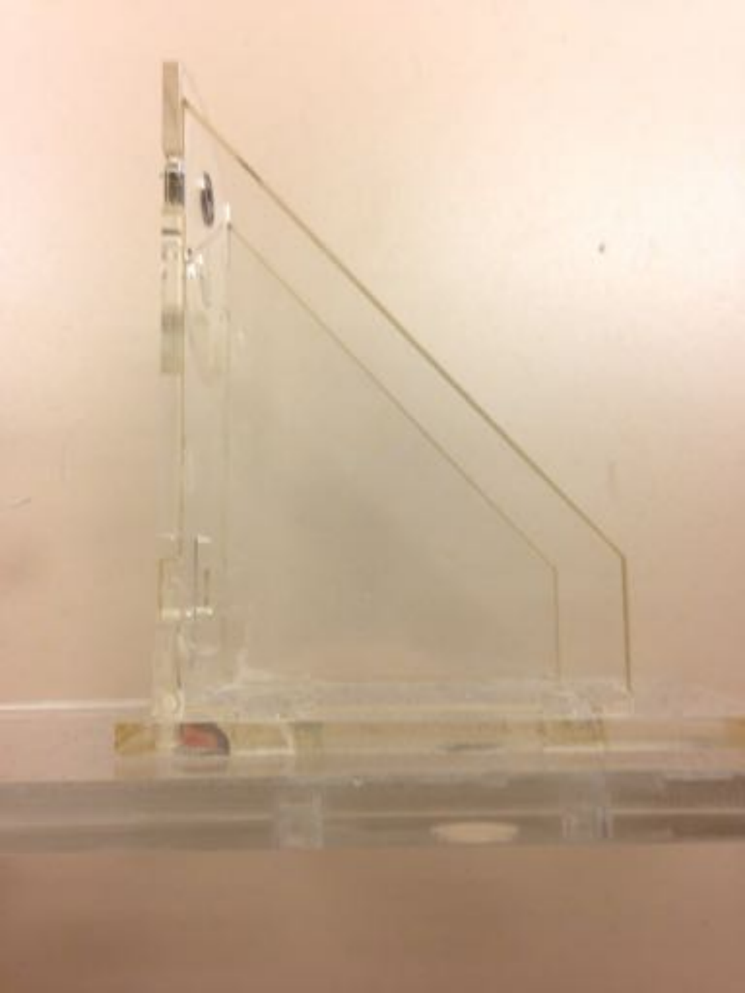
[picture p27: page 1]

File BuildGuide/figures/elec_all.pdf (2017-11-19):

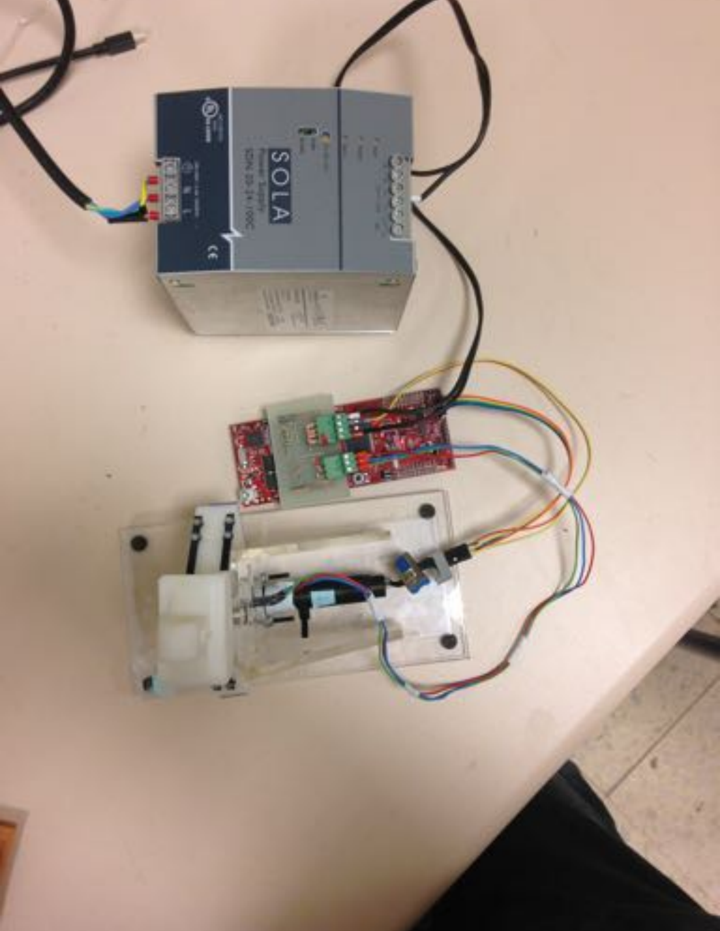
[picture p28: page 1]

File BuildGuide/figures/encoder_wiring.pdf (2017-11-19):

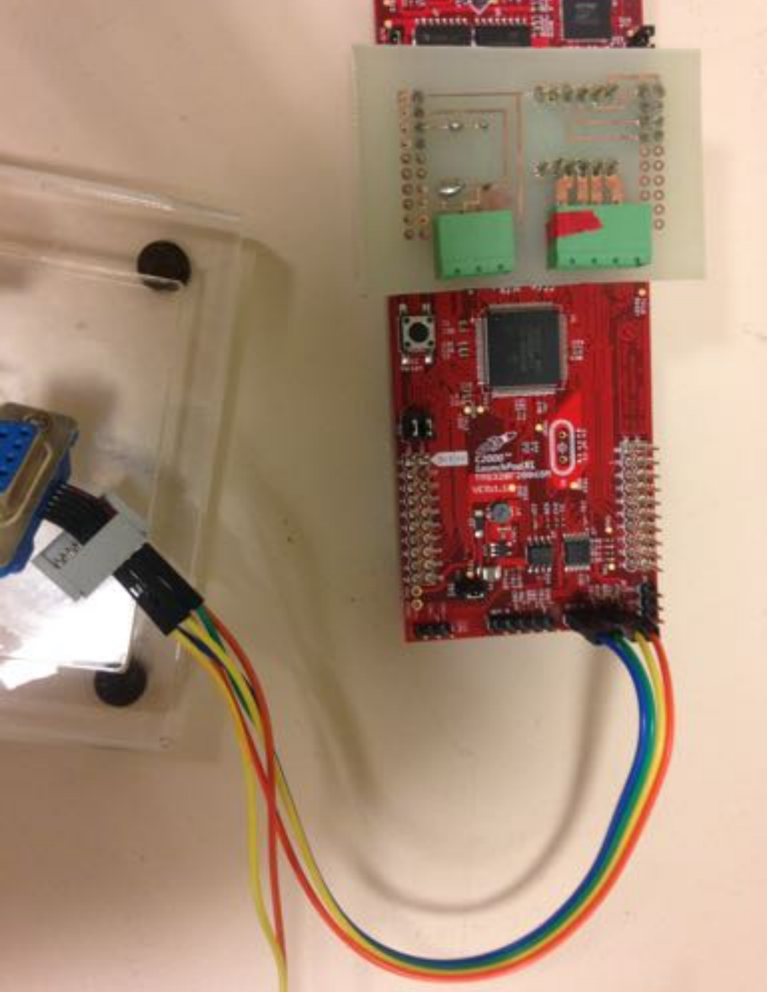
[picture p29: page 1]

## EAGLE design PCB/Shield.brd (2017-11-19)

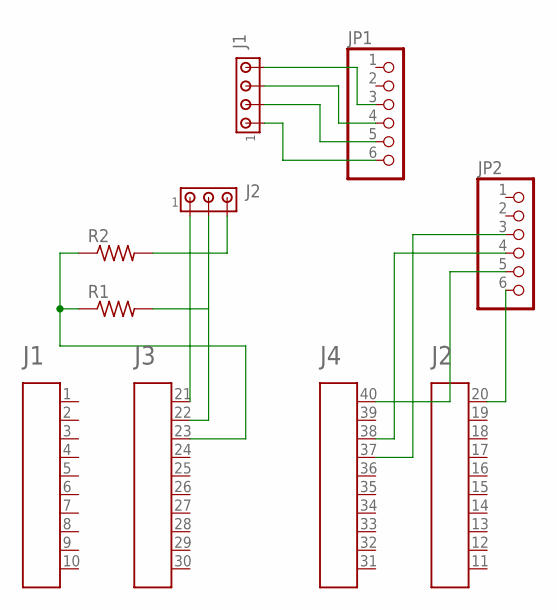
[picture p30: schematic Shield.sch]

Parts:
A1: HEADER4X10-BOOSTERPACK; 4X10-BOOSTERPACK
J1: MTA04-156; 1X4MTA
J2: MTA03-156; 1X3MTA
JP1, JP2: PINHD-1X6; 1X06
R1, R2: R-US_0207/10; 0207/10

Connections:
unnamed: A1.20, JP2.6
unnamed: A1.40, JP2.5
unnamed: A1.37, JP2.3
unnamed: A1.38, JP2.4
unnamed: A1.21, J2.1
unnamed: J1.1, JP1.6
unnamed: J1.2, JP1.5
unnamed: J1.3, JP1.4
unnamed: J1.4, JP1.3
unnamed: J2.3, R2.2
unnamed: A1.22, J2.2, R1.2
unnamed: A1.23, R1.1, R2.1

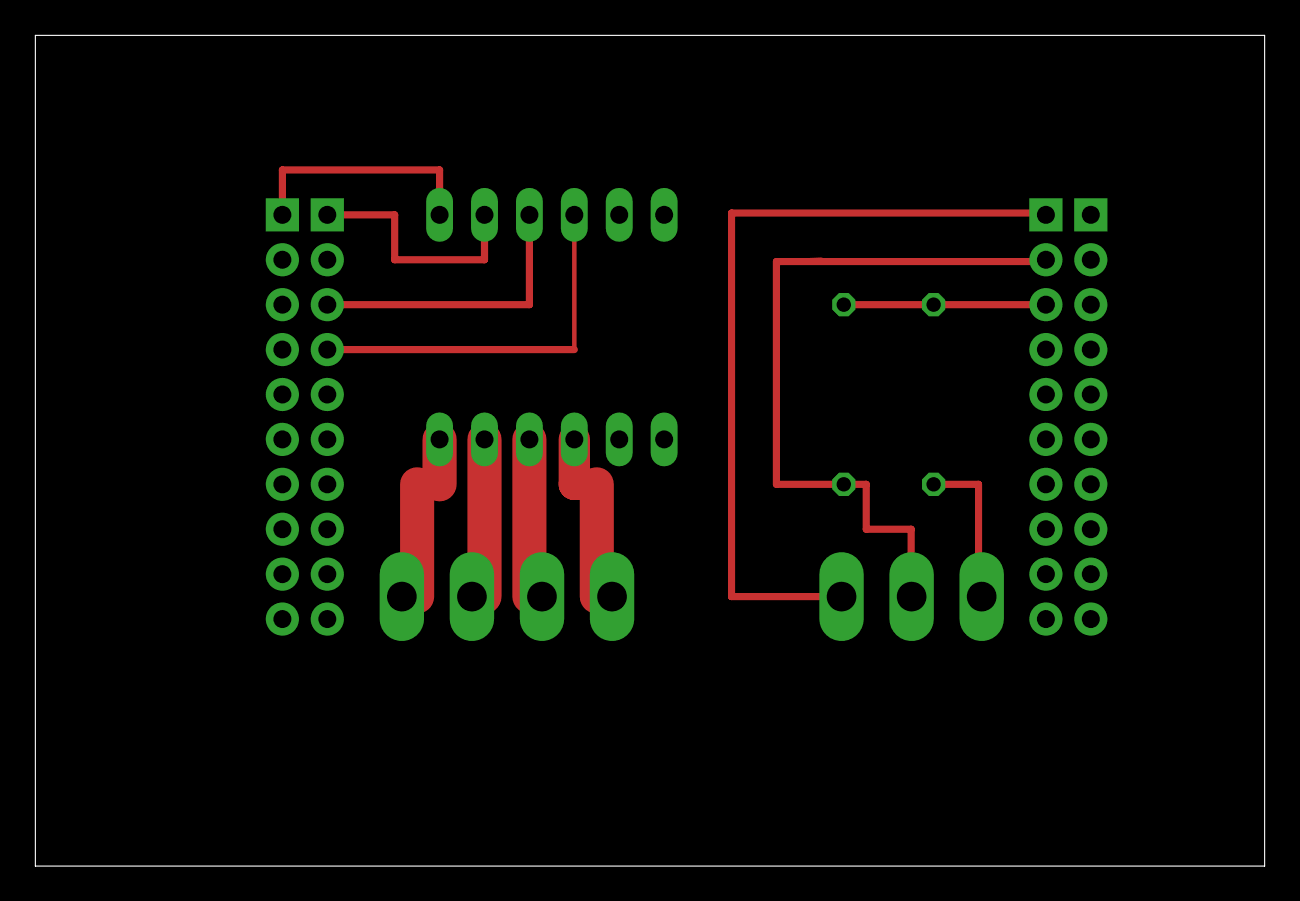
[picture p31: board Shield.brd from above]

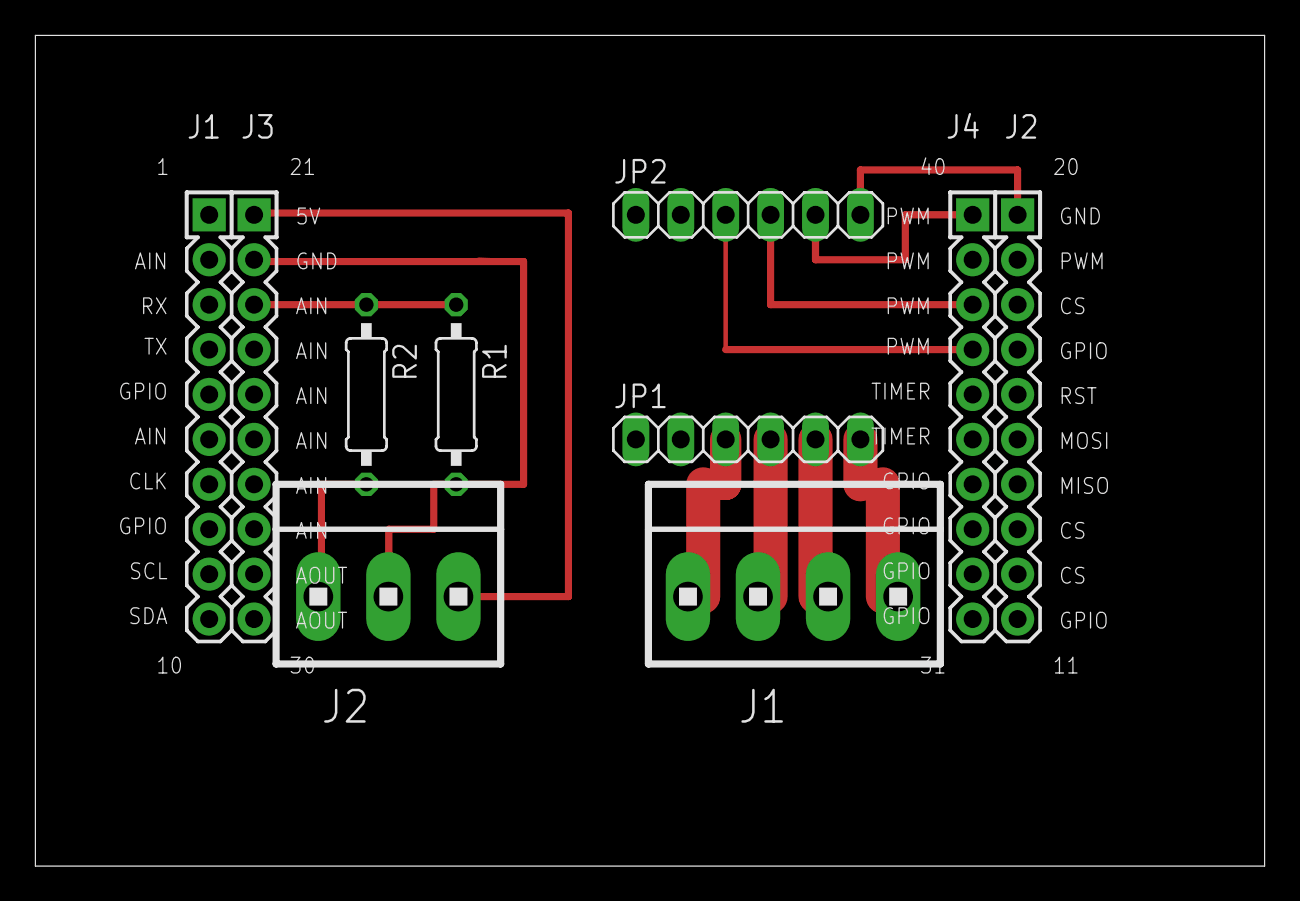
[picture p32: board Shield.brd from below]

Board: 2 copper layers, 69.5 x 47.0 mm, 7 parts (7 on the bottom side), 12 nets.
